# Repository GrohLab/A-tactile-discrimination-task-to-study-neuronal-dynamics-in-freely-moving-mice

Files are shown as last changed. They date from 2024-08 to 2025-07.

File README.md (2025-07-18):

#### Supplementary Materials for Heimburg, F., Saluti, N. M., Timm, J., Adlakha, A., Castelanelli, M., Klumpp M., Embray L., Both M., Draguhn A., Kuner T., Groh A. (2024). A tactile discrimination task to study neuronal dynamics in freely-moving mice.

**3D Model Files**: Contains 3D model blender files that show the proportions of the setup to scale.

**DataAndScripts**: Contains all required scripts and raw data (**.\RawData**) for replicating the figure legends.

**MaterialList**: Includes relevant setup items and experimental components necessary for reproducing the experiments.



The publication of the study can be found here: https://www.nature.com/articles/s41467-025-61792-0

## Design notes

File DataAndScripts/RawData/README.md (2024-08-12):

#### This folder contains the necessary raw data, used by the MATLAB scripts in the parent folder.

| File               | Description                                                                                      |
|--------------------|--------------------------------------------------------------------------------------------------|
|animalData.mat      |Conatins the read out of behavioral data, such as performance, trial number, or learning speed.   |
|AnimalData_CalciumImaging.mat      |Contains calcium imaging data for the sample session for the sample animal imaged with miniscope.   |
|decodingAccuracy_Ephys.mat      |Contains the decoding accuracies of lidocaine and control sessions. Rows resemble accuracies of different time windows, columns resemble the different recording areas (i.e., BC, VPM, POm, and ZIv).   |
|FrameInfo_OverviewVideo.mat      |Contains the animal's positional data from an exemplary video, in order to plot positional heat-maps and velocity plots.   |
|ROC_metrics_whiskerAngle.mat      |Contains the ROC metrics from the whisker angle decoding, from 100 bootstrapped runs.   |

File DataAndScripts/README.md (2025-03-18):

#### This folder contains all necessary Matlab files, used for obtaining the relevant figure data. Raw data is provided in a separate folder.

| File                                  | Description                                                                                                               |
|---------------------------------------|---------------------------------------------------------------------------------------------------------------------------|
| analyzePositionalData.m               | Loads the positional data from the RawData directory and generates a heat map of positional data and mean velocity plots. |
| Backlights.m                          | Compares population performance with and without backlights.                                                              |
| CNN_decoder_forCalciumImaging.m       | Code to train the CNN decoder and plot relevant figures in S3.                                                            |
| decreasing_contrast.m                 | Compares population performance across contrasts.                                                                         |
| Ephys_WhiskerMetrics.m                | Correlates ephys activity with behavioral metrics (e.g., whisker-angle, whisking-phase)                                   | 
| ExpNaive_TrialCount.m                 | Counts trials per animal for initial and reversed rule.                                                                   |
| Extinction.m                          | Compares population performance before and after extinction.                                                              |
| LearningInstability.m                 | Calculates the learning instability of mice with ablated BC.                                                              | 
| LearningSpeed.m                       | Compares learning speed and time between contrasts and between rules.                                                     |
| LearningSpeed_Cohort12.m              | Compares learning time for only cohort 12 (repeated rule switches)                                                        |
| Licking_Behavior.m                    | Analyzes and visualizes lick rates for mice across different stages of an experiment.                                     |
| Lidocaine.m                           | Compares population performance with and without lidocaine application.                                                   |
| NumSesperAnimal.m                     | Counts number of sessions per animal for initial and reversed rule.                                                       |
| onsetLatencyAnalysis.m                | Calculates the onset latency of ephys activity after aperture-touch.                                                      |
| Population_Analysis.m                 | Plots population performance over trials.                                                                                 |
| Population_Analysis_Cohort12.m        | Plots population performance over trials for only cohort 12 (repeated rule switches).                                     |
| Population_Analysis_Cohort16.m        | Plots population performance over trials for only cohort 16 (contrast 14 mm and 16 mm).                                   |
| Scripts_for_figures_calciumimaging.m  | Plot all the figures for Figure 3 calcium imaging data                                                                    |
| whiskerpluck.m                        | Compares population performance before and after whiskerpluck.                                                            |

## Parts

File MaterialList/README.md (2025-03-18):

### This table contains all materials, that were used throughout the course of the experiments. 

#### Linear Maze
| Product                                                                                      | Supplier                                        |
|----------------------------------------------------------------------------------------------|-------------------------------------------------|
| Linear track ([82 x 10 cm](Track%20complete%20with%20measurements.jpg), wood)                | Custom built, Lee Embray, Heidelberg            |
| Controlling unit of the behavioral apparatus (Arduino Uno R3 with firmata firmware)          | Arduino, assembled by Lee Embray, Heidelberg    |
| Metal wings (height: 205 mm, width: 97 mm, aluminum)                                         | Lee Embray, Heidelberg                          |
| [Controlling unit of the apertures with stepper motors](ApertureGate/info.md)                | Lee Embray, Heidelberg                          |

#### Lick ports adapted from Cornelius Schwarz, Tübingen
| Product                                                                                      | Supplier                                        |
|----------------------------------------------------------------------------------------------|-------------------------------------------------|
| Vasofix® Safety Braunüle® FEP G16                                                            | B. Braun SE, Melsungen, Germany                 |
| Piezo sensor (#285-784)                                                                      | RS components GmbH, Mörfelden-Walldorf, Germany |
| Analog-to-digital converter (ADC) to control lick ports                                      | Cornelius Schwarz, Tübingen                     |

#### Sensors and IR illumination 
| Product                                                                                      | Supplier                                        |
|----------------------------------------------------------------------------------------------|-------------------------------------------------|
| [Light beams](LightBeams/info.md)                                                            | Lee Embray, Heidelberg                          |
| LED strips for overhead illumination (Synergy 21 LED Flex Strip infrarot IR 12 12V IP65 Security Line 850nm, #140455) | ALLNET GmbH, Germering, Germany  |
| Backlight LEDs (HT-110IRPJ IR-Emitter 850 nm 140° 1204 SMD)                                  | Harvatek Corporation, Hsinchu, Taiwan           |
| Diffuser plate (3D printed with clear FLGPCL04 and sanded with P600)                         | Formlabs GmbH, Berlin, Germany                  |
| Diffuser film, 60% light diffusion (#DSF-10)                                                 | Folien Fischer UG, Hamburg, Germany             |

#### Intervention drugs
| Product                                                                                      | Supplier                                        |
|----------------------------------------------------------------------------------------------|-------------------------------------------------|
| Isoflurane (Isofluran Baxter)                                                                | Baxter Deutschland GmbH, Germany                |
| Buprenorphine (Bupresol vet. Multidose 0,3 mg/ml, 10 ml)                                     | CP-Pharma Handelsgesellschaft mbH, Burgdorf, Germany |
| Ketamine (100 mg/ml, 10 ml)                                                                  | CP-Pharma Handelsgesellschaft mbH, Burgdorf, Germany |
| Xylazine (Xylavet® 20 mg/ml)                                                                 | CP-Pharma Handelsgesellschaft mbH, Burgdorf, Germany |
| Lidocaine (Xylocaine® 1%)                                                                    | Aspen Pharma Trading Limited, Ireland           |
| ssAAV-1/2-hSyn1-chI-GCaMP6f-WPRE-SV40p(A)                                                    | Viral Vector Facility (VVF), Zürich, Switzerland|
| N-Methyl-D-aspartic acid, 98% (#AC329190500)                                                 | Thermo Fisher Scientific Inc., MA, USA          |

#### Cameras
| Product                                                                                      | Supplier                                        |
|----------------------------------------------------------------------------------------------|-------------------------------------------------|
| 2x High speed cameras (DMK 37BUX287)                                                         | The Imaging Source Europe GmbH, Bremen, Germany |
| Overview camera (DMK 37BUX290)                                                               | The Imaging Source Europe GmbH, Bremen, Germany |

#### Reward / punishment
| Product                                                                                      | Supplier                                        |
|----------------------------------------------------------------------------------------------|-------------------------------------------------|
| [Food dispensers](FoodDispensers/info.md)                                                    | Lee Embray, Heidelberg                          |
| 2 ml syringes (BD Discardit II)                                                              | Becton Dickinson GmbH, Heidelberg, Germany      |
| Tubes with Luer connector (#4256000)                                                         | B. Braun SE, Melsungen, Germany                 |
| Hifi integrated amplifier (A-S301)                                                           | Yamaha Music Europe GmbH, Rellingen, Germany    |
| 2x Speakers (Neo X 3.0 ribbon tweeter)                                                       | Fountek Electronics Co., Ltd, Zhejiang, China   |

#### EIB
| Product                                                                                      | Supplier                                        |
|----------------------------------------------------------------------------------------------|-------------------------------------------------|
| RHD USB Interface Board (#C3100)                                                             | Intan Technologies, CA, USA                     |
| Samtec Male Connector EIB (ST4-40-1.00-L-D-P-TR)                                             | Samtec Europe GmbH, Germering, Germany          |
| Samtec Female Connector Headstage (SS4-40-3.00-L-D-K-TR)                                     | Samtec Europe GmbH, Germering, Germany          |
| PCB (EIB and headstage)                                                                      | Custom built ([BRD file](EIB64-ST4-Multi.brd), printed by Multi-Circuit-Boards Ltd, Munich, Germany |
| Tungsten 99.95% CS Wire for Tetrodes (#100211)                                               | California Fine Wire Company, CA, USA           |
| Gold chloride solution for gold plating (200 mg/dL gold chloride in deionized water, HT1004-100ML) | Sigma-Aldrich, Inc., MO, USA              |
| Intan Interface 64 Channel Amplifier Chip (RHD2164)                                          | Intan Technologies, CA, USA                     |
| UV-curable adhesive (3M™ Filtek™ Supreme XTE)                                                | 3M Deutschland GmbH, Neuss, Germany             |
| Function generator (A365 Stimulus Isolator)                                                  | World Precision Instruments, Inc., FL, USA      |
| Electric Rotary Joint (AHRJ-OE_2x2_AD_200-0.22_24_USB-C)                                     | Doric Lenses Inc., Quebec City, Canada          |

#### Miniscope
| Product                                                                                      | Supplier                                        |
|----------------------------------------------------------------------------------------------|-------------------------------------------------|
| Miniscope V4 main body (Excitation, objective, and emission module)                          | Custom print from Heidelberg precision mechanics workshop/ Open Ephys |
| V4 Base Plate                                                                                | Custom print from Heidelberg precision mechanics workshop/ Open-Ephys |
| Rigid-Flex PCB                                                                               | Open-Ephys                                      |
| Optical Filters <br> - Excitation filter 4mm x 4mm, ET474/40x <br> - Emission filter 4mm x 4mm, ET525/50m <br> - Dichroic mirror 6mm x 4mm, T495lpxr | Chromal/Open-Ephys |
| Lenses <br> - 2 x 3mm diameter, 6mm FL achromat used in the objective module (#45-089) <br> - 4mm diameter, 10mm FL achromat used in the emission module (#63-691) <br> - Half-ball Lens, 3.0mm Diameter, N-BK7 (#47-269)                                    | Edmund Optics/Open-Ephys                        |
| Coax cable, 36AWG 26/50SPC                                                                   | Cooner Wire                                     |
| Hirose U.FL Connector, U.FL-PR-SMT2.5-1(10)                                                  | Mouser                                          |
| GRIN Lenses, ProView™ Lens Probe, 0.5mm diameter, ~4.0mm length                              | Inscopix                                        |

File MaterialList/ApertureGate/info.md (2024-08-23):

# Adjustable Aperture Gate

## Description

The Adjustable Aperture Gate is designed to produce multiple programmable apertures between two sliding doors for use in rodent behaviour experiments.
The various apertures can be pre programmed using the programming module, the programming module can then be used to test the operations using the DIP switches on it's front panel,
once the programming module is disconnected and the unit connected to experiment controller (external controller) these preset distances between the sliding doors can then be
 recalled using three 5V TTL (Transistor-Transistor-Logic) or 3.3V logic inputs driven by a single board computer (Raspberry Pie or Arduino for example) or any other microprocessor or logic controller.

The unit requires a 12V power supply and three logic control inputs with ground, a simple three bit binary word input will recall the various presets causing the sliding doors to move to the selected distance.

The design has two parts, the **Programming Module** (LCD/Buttons) and the **Gate Unit** (Mechanical/Main PCB) which are connected together using a standard one-to-one 15pin D type male to female cable.
The LCD and switches are mounted in a small housing allowing parameter changes without disturbing the experiment.
The Gate Assembly unit is designed using Google Sketchup and 3D printed using a FormLabs Form 2 SLA (Stereolithografie) 3D printer,
assembly of the mechanical parts is quite labour intensive and modification of the motor for this application requires the use of a lathe.

The Programming Module only needs to be connected to change the preset aperture or to run tests to check operation, all changes are then saved to non volatile memory in the Gate Unit and the Gate
Unit can then run without the programming module.
Therefore only one Programming Module is necessary to operate multiple Gate Units.

## Programming Module

## Parts List 1

|Part | Qty |Part Description  | Manufacturer | Part ID | Order URL |
| ---- | --- | ----------------- | ------------ | ------- | --------- |
| J1 | 1 | DSUB 15M connector | MH Connectors | 746751 | [Conrad](https://www.conrad.de/de/p/mh-connectors-mhdb15-sp-2101-0180-02-d-sub-stiftleiste-180-polzahl-num-15-loetkelch-1-st-746751.html) |okw-soft-case-d9052288-wall-mount-enclosure-desktop-case-73-x-117-x-27-acrylonitrile-butadiene-styrene-lava-volcano-1-531612) |
| LCD1 | 1 | LCD 16x2 White on Blue  | Gleichmann | 183045 | [Conrad](https://www.conrad.com/p/gleichmann-led-component-white-blue-w-x-h-x-d-80-x-36-x-132-mm-ge-c1602b-tmi-jtr-183045) |
| SW1-4 | 4 | Momentary Switch TC-D6SW  | TRU COMPONENTS | 2238782 | [Conrad](https://www.conrad.de/de/p/tru-components-tc-d6sw-impulstaster-35-v-dc-0-01-a-tastend-1-st-1589415.html) |
| DSW1 | 1 | DIP Switch 4 Way  | APEM | 700640 | [Conrad](https://www.conrad.com/p/apem-nds-04-v-dip-switch-standard-700640) |
| R1 | 1 | Resistor 56 Ohm 1/4W | Yageo | 1417715 | [Conrad](https://www.conrad.com/p/yageo-cfr-25jt-52-56r-carbon-film-resistor-56-axial-lead-0207-025-w-5-1-pcs-1417715) |
| R2,3,4 | 3 | Resistor 2.2k Ohm 1/4W | Yageo | 1417683 | [Conrad](https://www.conrad.com/p/yageo-cfr-25jt-52-2k2-carbon-film-resistor-22-k-axial-lead-0207-025-w-5-1-pcs-1417683) |
| RV1 | 1 | Trim Potentiometer 10k Ohm 1/4W  | Vishay | 423980 | [Conrad](https://www.conrad.com/p/vishay-t63yb103kt20-t63yb103kt20-multi-grade-trim-potentiometer-423980) |
| PCB | 1 | Strip Board Paper/Copper 2.54mm | Rademacher | 529531-62 | [Conrad](https://www.conrad.de/de/p/rademacher-wr-typ-710-2-platine-hartpapier-l-x-b-100-mm-x-75-mm-35-m-rastermass-2-54-mm-inhalt-1-st-529531.html) |
| Case | 1 | Case 73x117x27mm  | OKW | 531612 | [Conrad](https://www.conrad.com/p/okw-soft-case-d9052288-wall-mount-enclosure-desktop-case-73-x-117-x-27-acrylonitrile-butadiene-styrene-lava-volcano-1-531612) |

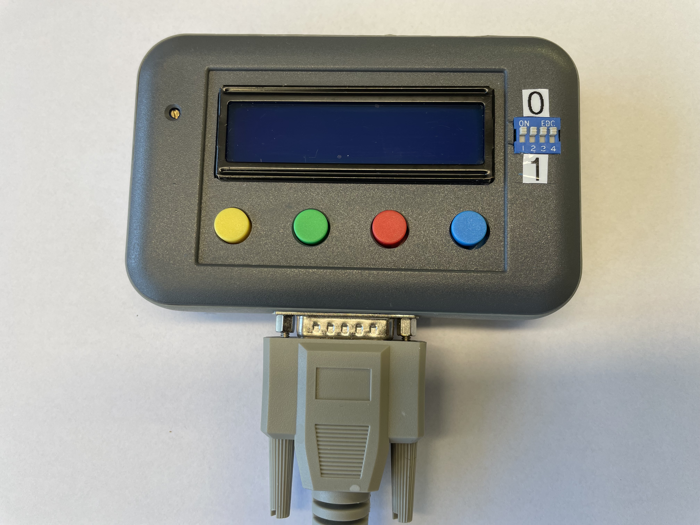
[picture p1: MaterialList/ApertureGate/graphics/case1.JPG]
programmer Case
<br/>**Programming Module**

The programming module is created using the following schematic, a small piece of strip board is used to mount the four main switches as shown in the picture below.
All components are mounted directly onto the LCD or switches therefore no PCB is necessary for the programming module.
The potentiometer RV1 is used to adjust the contrast on the LCD and is required to be set only once.
D1 is the backlight that is built into the LCD module and connected using pins 15 and 16 of the LCD module.

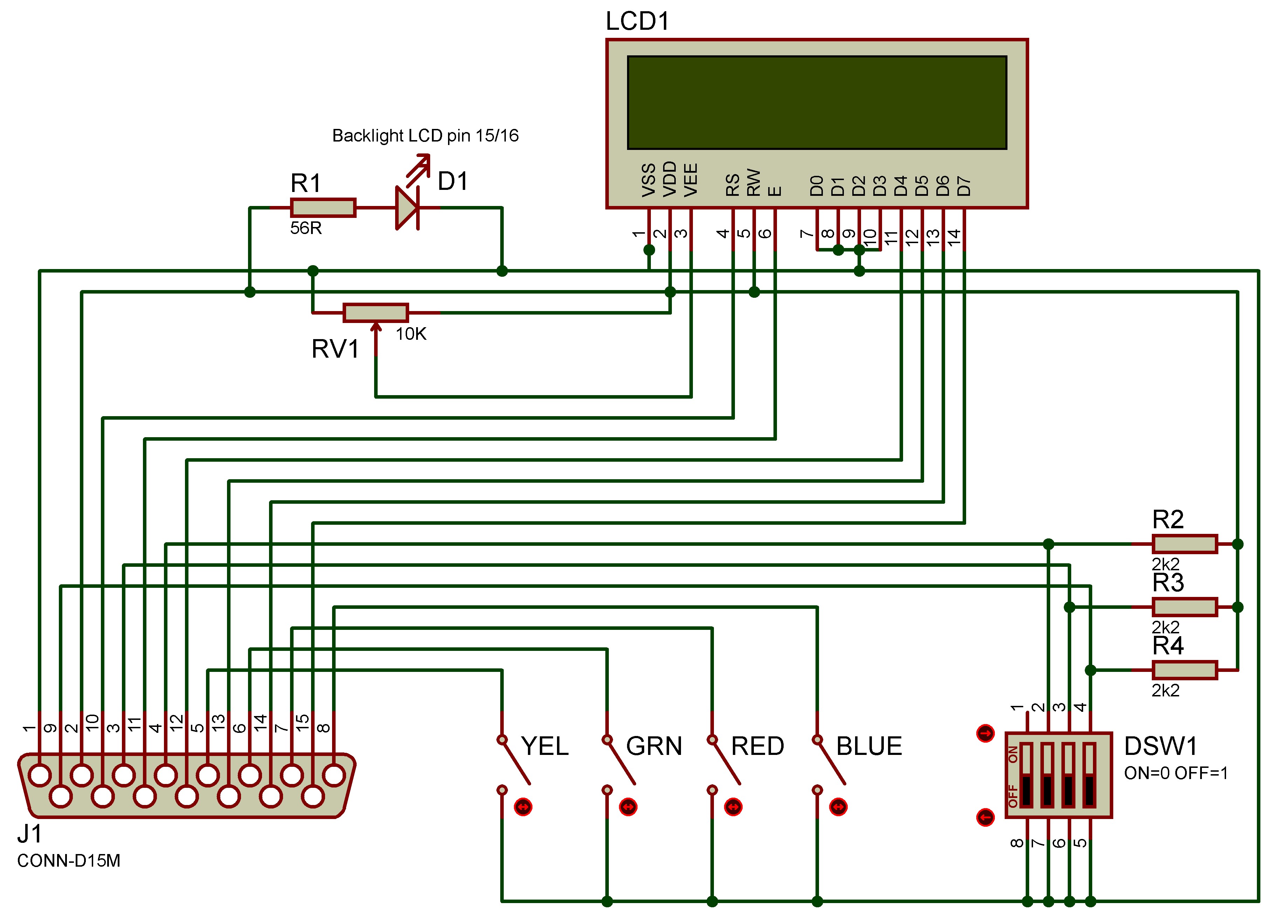
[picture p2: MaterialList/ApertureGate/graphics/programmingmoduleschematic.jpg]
Programming Module Schematic
<br/>**Programming Module Schematic**

All components are mounted in a plastic housing and necessary holes for the the LCD, switches and connectors are drilled accordingly.

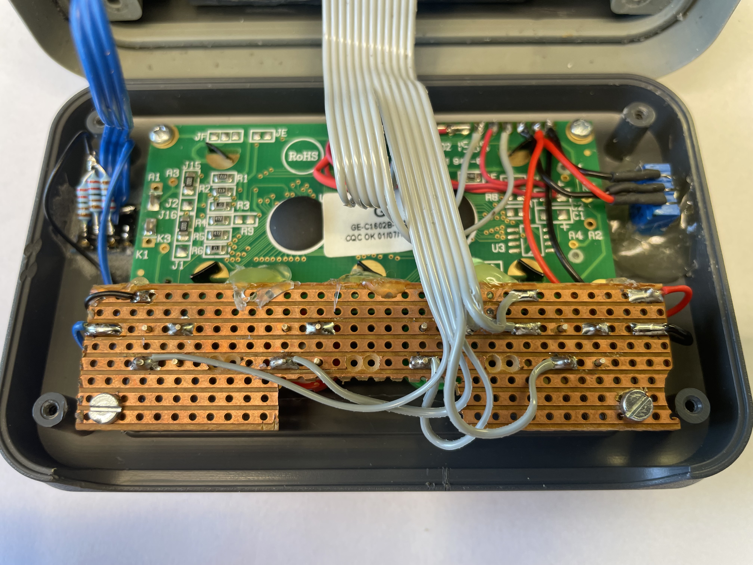
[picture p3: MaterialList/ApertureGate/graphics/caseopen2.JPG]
case open2
<br/>**Programming Module - Open**

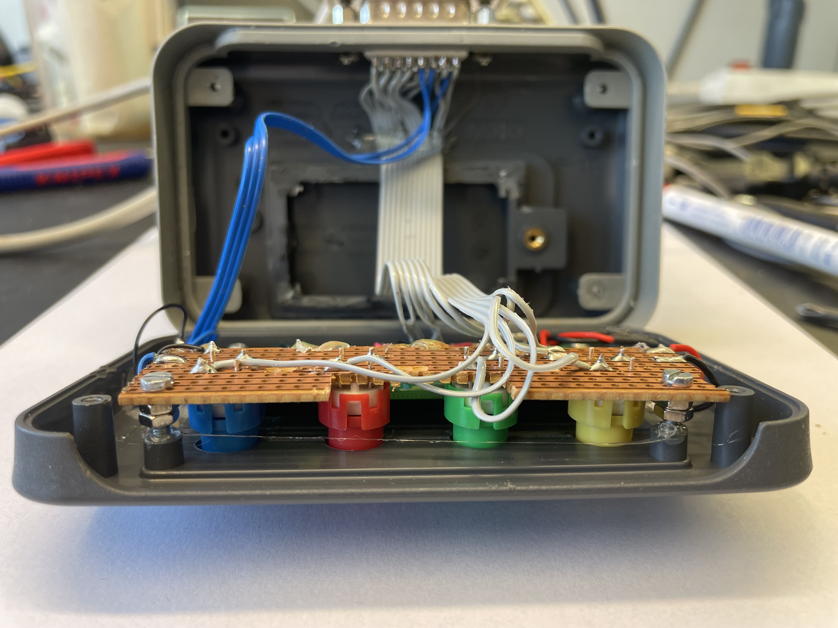
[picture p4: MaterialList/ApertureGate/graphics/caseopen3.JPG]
case open3
<br/>**Programming Module - Button Mounting**

## Gate Unit

## Parts List 2

|Part | Qty |Part Description  | Manufacturer | Part ID | Order URL |
| ---- | --- | ----------------- | ------------ | ------- | --------- |
| U1 | 1 | Microchip PIC18F23K20 MPU | Microchip  | 666-9860 | [RS Components](https://de.rs-online.com/web/p/mikrocontroller/6669860) |
| U2 | 1 | L297D Stepper Motor Driver SOIC | STMicroelectronics  | 102-3535  | [RS Components](https://de.rs-online.com/web/p/motor-treiber-ics/1023535) |
| U3 | 1 | L298P013TR Dual Full Bridge Driver | STMicroelectronics | 880-5308 | [RS Components](https://de.rs-online.com/web/p/motor-treiber-ics/8805308) |
| U4 | 1 | SMD 3.3V Regulator TLV111733 | Texas Instruments | 923-3827 | [RS Components](https://de.rs-online.com/web/p/spannungsregler/9233827) |
| U5 | 1 | L78S05CV 5V Regulator TO220 | STMicroelectronics  | 179345  | [Conrad](https://www.conrad.de/de/p/stmicroelectronics-l78s05cv-spannungsregler-linear-typ78-to-220ab-positiv-fest-5-v-2-a-179345.html) |
| D1-8 | 8 | Schottkey Diode SK26L | PanJit | 1304995 | [Conrad](https://www.conrad.de/de/p/panjit-schottky-diode-gleichrichter-sk26l-do-214aa-60-v-einzeln-1304995.html) |
| R1,2 | 2 | Resistor SMD 1206 1 Ohm 1/2W | Panasonic | 1473248 | [Conrad](https://www.conrad.de/de/p/panasonic-erj-8bqf1r0v-dickschicht-widerstand-1-smd-1206-0-5-w-1-200-ppm-c-1473248.html) |
| R3 | 1 | Resistor SMD 0805 22k Ohm 1/8W| Tru Components | 1584677 | [Conrad](https://www.conrad.de/de/p/dickschicht-widerstand-22-k-smd-0805-0-125-w-5-100-ppm-c-tru-components-tc-0805s8j0223t5e203-1-st-1584677.html) |
| R5 | 1 | Resistor SMD 0805 3.3k Ohm 1/8W| Tru Components | 1584493 | [Conrad](https://www.conrad.de/de/p/tru-components-tc-0805s8f3301t5e203-dickschicht-widerstand-3-3-k-smd-0805-0-125-w-1-100-ppm-c-1-st-tape-cut-1584493.html) |
| R4,6-13 | 9 | Resistor SMD 0805 2.2k Ohm 1/8W| Tru Components | 1584491 | [Conrad](https://www.conrad.de/de/p/tru-components-tc-0805s8f2201t5e203-dickschicht-widerstand-2-2-k-smd-0805-0-125-w-1-100-ppm-c-1-st-tape-cut-1584491.html) |
| C1 | 1 | Capacitor SMD 0805 3300pF | Thomsen | 460338 | [Conrad](https://www.conrad.de/de/p/thomsen-keramik-kondensator-smd-0805-3300-pf-50-v-10-1-st-tape-cut-460338.html) |
| C2,3,5,7 | 4 | Capacitor SMD 0805 100nF 50V  | Samsung | 454108 | [Conrad](https://www.conrad.de/de/p/samsung-electro-mechanics-cl21b104jbcnnnc-keramik-kondensator-smd-0805-100-nf-50-v-5-4000-st-tape-on-full-reel-454108.html?searchType=SearchRedirect) |
| C4 | 1 | Elecrolytic Capacitor 470uF 16V| Yageo | 445373 | [Conrad](https://www.conrad.de/de/p/yageo-se016m0470b3f-0811-elektrolyt-kondensator-radial-bedrahtet-3-5-mm-470-f-16-v-20-x-h-8-mm-x-12-mm-1-st-445373.html) |
| C6 | 1 | Elecrolytic Capacitor 100uF 16V| Yageo | 445579 | [Conrad](https://www.conrad.de/de/p/yageo-s5016m0100bzf-0605-elektrolyt-kondensator-radial-bedrahtet-2-5-mm-100-f-16-v-20-x-h-6-mm-x-5-mm-1-st-445579.html) |
| J1-6 | 4 | Pin Strip Header 8Pin Male| BKL Electronic | 742235-VQ | [Conrad](https://www.conrad.com/p/bkl-electronic-10120504-straight-nominal-current-details-3-a-742235) |
| J1-6 | 4 | Pin recepticle 8Pin Female | TRU COMPONENTS | 1560801 | [Conrad](https://www.conrad.com/p/tru-components-receptacles-precision-no-of-rows-1-pins-per-row-8-tc-0306pf-008-1-50-00-1-pcs-1560801) |
| J7 | 1 | D15F connector | MH Connectors | 746800 | [Conrad](https://www.conrad.de/de/p/mh-connectors-mhdb15-ss-2101-0180-12-d-sub-buchsenleiste-180-polzahl-num-15-loetkelch-1-st-746800.html) |
| J8 | 1 | Low Power connector Socket 2.1mm 5.5mm | BKL Electronic | 733946 | [Conrad](https://www.conrad.com/p/bkl-electronic-072335-low-power-connector-socket-vertical-vertical-55-mm-21-mm-1-pcs-733946) |
| PSU | 1 | Powersupply 12V 3A  | Mean Well | 1439200 | [Conrad](https://www.conrad.de/de/p/mean-well-gst36e12-p1j-steckernetzteil-festspannung-12-v-dc-3000-ma-36-w-1439200.html) |
| M1 | 1 | Stepper Motor 0.25Nm 0.6A | EMIS | 198398 | [Conrad](https://www.conrad.de/de/p/emis-schrittmotor-103-h5205-0351-103-h5205-0351-0-25-nm-0-6-a-wellen-durchmesser-5-mm-198398.html) |
| SW5,6 | 2 | Microswitch125V AC 3A| Hartmann | 704713 | [Conrad](https://www.conrad.de/de/p/hartmann-mikroschalter-microhart-125-v-ac-3-a-1-x-ein-ein-tastend-1-st-704713.html) |
| Tube 5mm | 1 | Brass Tube 5mmx500mm  | REELY | 221794 | [Conrad](https://www.conrad.com/p/brass-tube-rail-x-l-5-mm-x-500-mm-inside-diameter-3-mm-1-pcs-221794) |
| Rod 6mm | 1 | Silver Steel Rod 6mmx500mm  | REELY | 237086 | [Conrad](https://www.conrad.com/p/reely-silver-steel-shaft-x-l-6-mm-x-500-mm-237086) |
| Collared Bush | 2 | ID-6mm OD-10/15mm  | REELY| 237043 | [Conrad](https://www.conrad.com/p/reely-collared-bush-inside-diameter-6-mm-outside-diameter-10-mm-width-15-mm-1-pcs-237043) |
| Spindle | 1 | RH Threaded Spindle TSR-Tr 5x1.5  | HFB| 12-0515-01 | [HFB](https://hfbshop.de/?cat=c27_TSR-1500mm-Rechts-TSR-1500mm-Rechtsgewinde.html) |
| Spindle | 1 | LH Threaded Spindle TSR-Tr 5x1.5  | HFB| 12-0515-02 | [HFB](https://hfbshop.de/?cat=c30_TSR-1500mm-Links-TSR-1500mm-Linksgewinde.html) |
| Spindle Nut | 1 | RH Nut 5x1.5 | HFB| 33-0515-01 | [HFB](https://hfbshop.de/product_info.php?info=p5076_sechskant-messingmutter-rohling-skm-ms-tr-5x1-5-rechts.html) |
| Spindle Nut | 1 | LH Nut 5x1.5  | HFB| 33-0515-02 | [HFB](https://hfbshop.de/product_info.php?info=p5098_sechskant-messingmutter-rohling-skm-ms-tr-5x1-5-links.html) |
| Bearing | 2 | Radial 3x10x4  | REELY | 215210 | [Conrad](https://www.conrad.com/p/reely-radial-ball-bearing-chrome-steel-inside-diameter-3-mm-outside-diameter-10-mm-rotational-speed-max-60000-um-215210) |
| Cable | 1 | D-Sub15 Cable M-F 1M  | Pheonix Contact | 673800 | [Conrad](https://www.conrad.de/de/p/phoenix-contact-seriell-parallel-anschlusskabel-1x-d-sub-buchse-15pol-1x-d-sub-stecker-15pol-1-00-m-weiss-673800.html) |
| Wire | 1 | Jumper Wire 1x0.2mm  | Tru Components | 1567899 | [Conrad](https://www.conrad.de/de/p/tru-components-1567899-schaltdraht-yv-1-x-0-20-mm-schwarz-100-m-1567899.html) |

## 1. PCB Assembly

PCB Gerber files are supplied allowing production and ordering, the origional Proteus design file is also supplied incase any modifications for specific requirements are necessary.
All components of the PCB are mounted by hand and special attention should be applied to the motor driver (U3) as the underside of the component is used as a heat sink and must be soldered to the PCB,
this is done from the reverse side of the PCB using the through holes integrated on the PCB design. Soldering SMD devices by hand requires some experience.

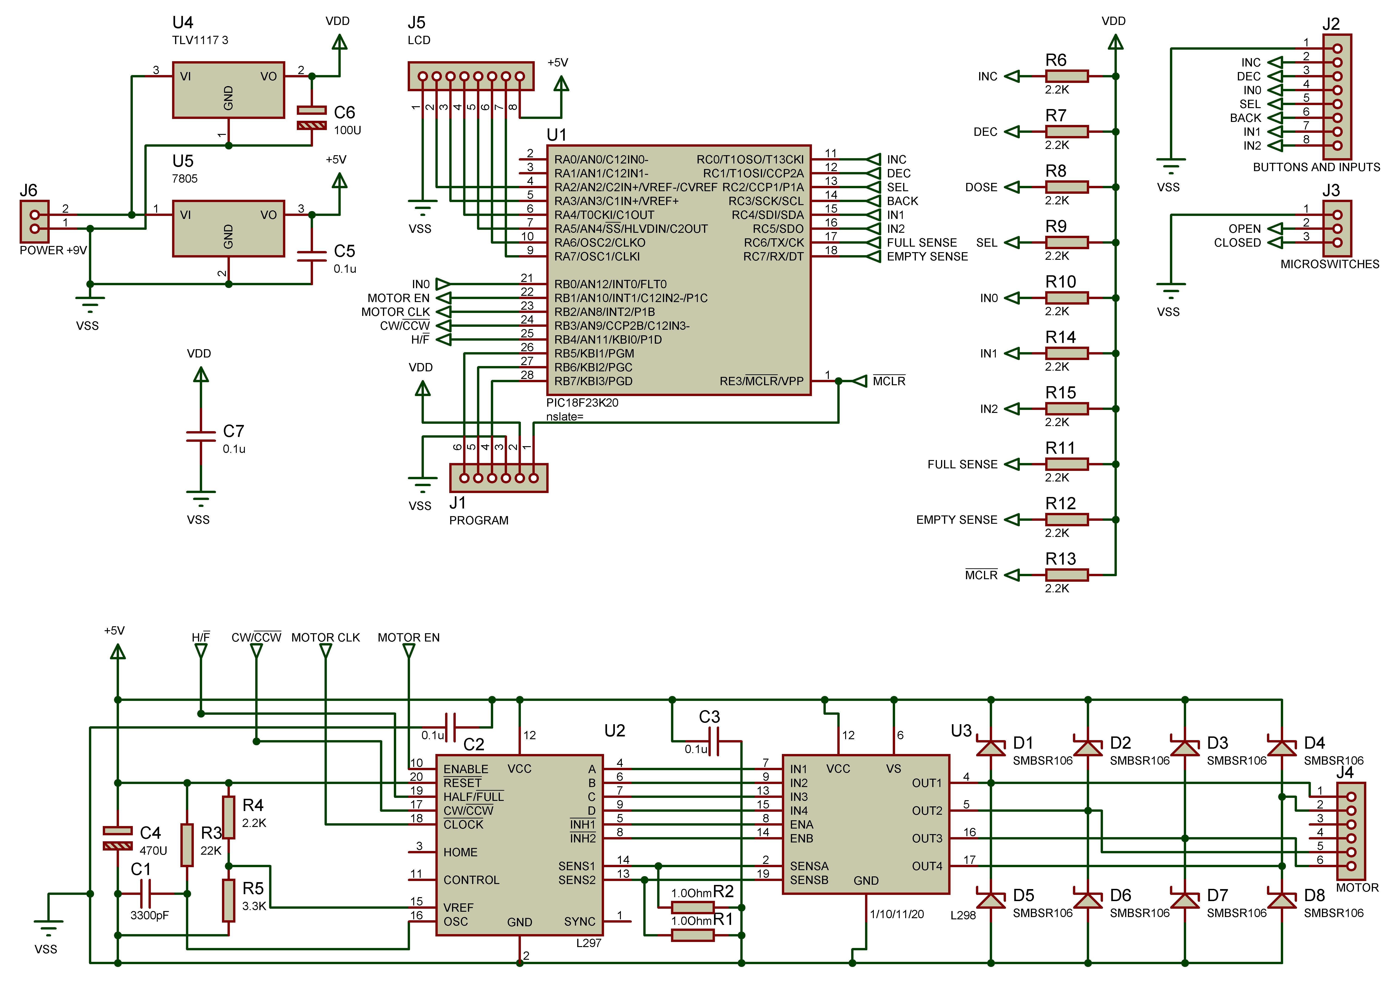
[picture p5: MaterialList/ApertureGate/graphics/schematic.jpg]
schematic
<br/>
**Main PCB Schematic**

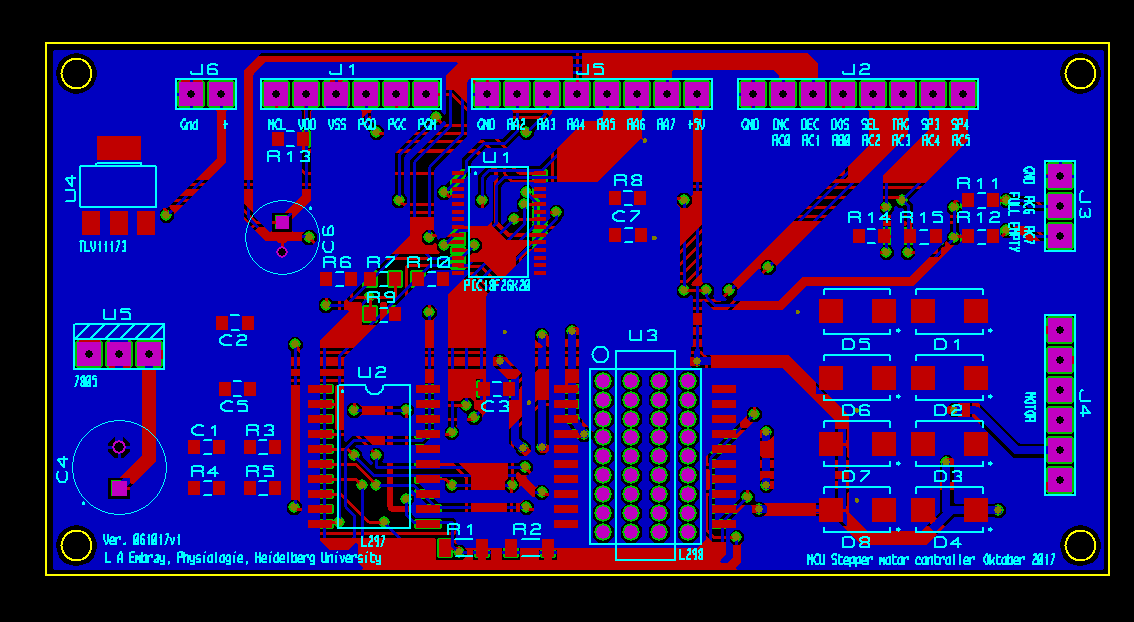
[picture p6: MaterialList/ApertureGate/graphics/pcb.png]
pcb
<br/>
**Main PCB Layout**

## 2. Programming

The Microprocessor must be programmed with the included program, this is performed using a Microchip Pickit 3 In-Circuit Debugger/Programmer and the Microchip MPLAB IDE X software.
once the included project is added to the programming software the PicKit programmer can be plugged directly into the J1 on the main PCB and the program uploaded to the microprocessor.

## 3. Parts Preparation

The output shaft of the motor **(22)** requires modification, this is best performed on a lathe, The motor should be carefully dismantled and the rotor removed.

1. Using a lathe the shaft of the rotor should be shortened to the same length as the shorter side of the rotor meaning the assembled motor has no protruding shaft from either side.
2. Using a lathe the complete length of the rotor/shaft should be drilled out using a 2.5mm drill bit mounted in the tailstock,
3. it is very important that the drilling is centered correctly for smooth operation and this can be achieved by using a centre drill first as a guide before the 2.5mm drill bit.
4. Using a lathe an M3 thread must be cut within the hole drilled in step two, the M3 Tap should be mounted in the tailstock and the tailstock should be freely moving on the guide ways,
5. by manually turning the main spindle chuck holding the rotor the thread can be accurately cut through the entire length of the rotor shaft.
6. The motor should now be reassembled paying particular care to making sure there is no small pieces of metal swarf trapped within and all parts are sufficiently clean,
7. any dirt or swarf will cause the motor to jam.

The two Silver Steel Shafts **(17)** should be cut to a length of 202mm, using a lathe the ends of the shafts should be drilled to a depth of 10mm using a 3.3mm drill,
these holes should then be tapped using a M4 tap.

A piece of 5mm brass tube **(6)** should be cut to a length of 72.5mm, this is used to carry and protect the two wires that connect to the end of travel switch **(4)** as shown in the picture below.

The left and right threaded rods (8,18) should be cut to a length of 88mm.

1. Using a lathe 4mm of the ends of the rods should be reduced in diameter to 3mm.
2. Using a lathe, 10mm of the opposite end of the rods should be reduced to a diameter of 3mm.
3. Using a lathe and an M3 die the 10mm end should have a M3 thread cut.

Once all parts are 3D printed a small amount of cleaning/trimming and sanding is required to allow all parts to accurately fit together without force. The following drawing shows all parts for assembly.

The four motor mount holes on the Main Body **(12)** should be counter sunk to allow for flush mounting of the motor allowing the slider **(10)** to travel up against the Main Body **(12)** without obstruction.

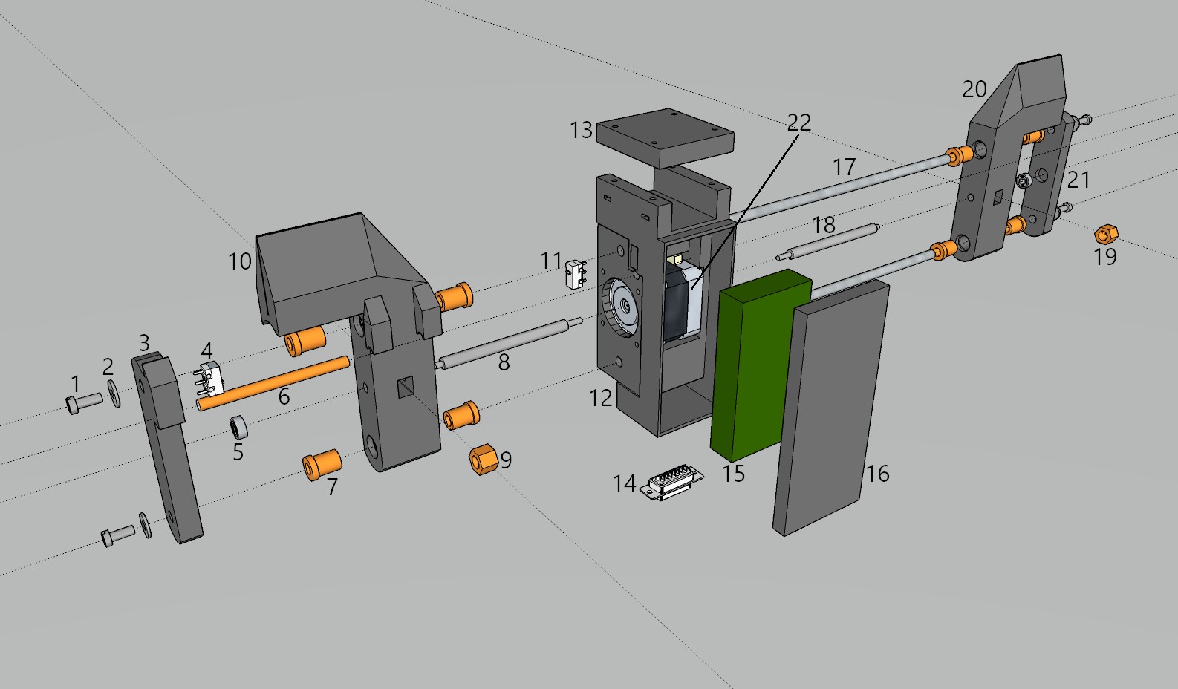
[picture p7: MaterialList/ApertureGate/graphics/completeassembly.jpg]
<br/>
**Complete Assembly**

## Key To Drawing

1. M4x10mm Screw x4
2. M4 Washer x4
3. Left Slider Stop
4. End of Travel Micro Switch
5. Bearing Radial 3x10x4 x2
6. Brass Tube 5x72.5mm
7. Collared Bush 6x10x15mm x8
8. Left Hand Threaded Rod
9. Left Handed Brass Nut 5x1.5
10. Left Slider
11. Start of Travel Micro Switch
12. Main Body
13. Mounting Clamp
14. D15 Female Connector
15. Assembled Printed Circuit Board
16. PCB Cover
17. Silver Steel Shaft 6x202mm x2
18. Right Hand Threaded Rod
19. Right Handed Brass Nut 5x1.5
20. Right Slider
21. Right Slider Stop
22. Motor

## 4. Assembly of parts

1. The Motor **(22)** is inserted into the Main Body **(12)** and fixed in place with the wires facing upwards using four M3x10 counter sunk screws.

2. The two Silver Steel Shafts **(17)** are inserted into the Main Body **(12)** with equal lengths of the shaft protruding from each side of the Main Body **(12)**,
these should now be fixed in place using cyanoacrylate glue being careful not to get any excess glue on the Shafts **(17)**.

3. The two End Stop Microswitches **(4/11)** should be prepared by soldering two 0.05mm wires of 15cm length to each of of the Microswitches normally open contacts(no).

4. One Microswitch **(11)** can now be mounted into its cutout on the Main Body **(12)** and the wires threaded through to the PCB cavity inside the Main Body **(12)**,
the second Microswitch can now be inserted into the cutout on the Left Slider Stop **(3)** and the wires threaded through the channel inside the Left Slider Stop **(3)**,
for the time being the wires should be left long and will later be attached.

5. The eight Collared Bushes **(7)** should be carefully pressed into the Left and Right Sliders **(10/20)**, it is important that these are inserted straight and true,
this is best done using either a press or a machine vice using a scrap piece of the 6mm silver steel shaft as a guide,
opposing bushes should be pressed into place at the same time with the 6mm shaft inserted into both bushes as this will guarantee alignment during insertion.

6. The Left Handed and Right Handed Threaded rods **(8/18)** can now be attached to the Motor **(22)**,
the 10mm of M3 thread on the threaded rod should be screwed into the motors shaft using thread lock to be sure they don't unscrew.

7. The two Bearings **(5)** are to be pressed into the Left and Right Slider stops **(3/21)** this is easily accomplished using a machine or bench vice.

8. The Left and Right Hand Threaded Brass Nuts **(9/19)** can be installed into the Left and Right Sliders **(10/20)**,
the nuts should not be a tight fit but also should not have any excessive play as this will affect the accuracy of the aperture,
however a small amount of movement must be available to allow for slight inaccuracies in the Threaded Rods **(8/18)**.

9. The two Sliders **(10/20)** can now be slid onto the two Silver Steel Shafts **(17)** and with the Left and Right Handed Brass nuts **(9/19)** held in place can be slid until the
Brass Nuts come into contact with the Left and Right Handed Threaded Rods **(8/18)**.

10. By applying a small amount of pressure to both Sliders **(10/20)** and turning the Motor Shaft both the sliders will be drawn in towards the motor,
it is important that both Sliders arrive at the Main Body **(12)** at the same time, the Microswitch **(11)** should be heard to click just before the Sliders come into hard contact with the Main Body.

11. The Right Slider Stop **(21)** can now be fitted to the end of the Silver Steel Shaft **(17)** paying attention that the end of the Right Hand Threaded rod **(18)** is inserted into the
Bearing **(5)**, This can now be fixed in place using two M4x10 screws and washers **(1/2)** holding the Slider Stop to the two Shafts.

12. The Left Slider Stop **(3)** is mounted in exactley the same way with one exception,
the wires from the End Stop Microswitch **(4)** which were earlier threaded though the Left Slider Stop should now be threaded through the Brass Tube **(6)** and as the slider stop is brought into
place this tube should be inserted into the available holes on the Left Slider Stop **(3)** and the Main Body **(12)**, approximately 2.5mm of each end of the Brass Tube should be inserted.
The microswitch wire should be threaded through to the Main Body PCB cavity. The Slider Stop should be fixed into place using two M4x10 screws and washers **(1/2)**.

13. By turning the Motor/Threaded Rods the assembly can be checked for smooth operation and that the microswitches are pressed before the sliders make hard contact at either end of their travel,
a small amount of machine oil or grease should be applied to the threaded rods and also to the silver steel shafts.

14. The PCB **(15)** can now be placed within the cavity in the Main Body **(12)** with the wires from the two Microswitches **(4/11)** and Motor **(22)** exiting above the PCB.
The PCB **(15)** is a tight fit inside the Main Body **(12)** and does not require and additional fixing.

15. The wires from the Motor **(22)** should be cut and spliced (shortened) to a length that easily reaches the motor connector **(J4)** at the top of the PCB **(15)** without too much excess length,
this is now plugged into the motor connector **(J4)**.

16. The wires from the End Stop Microswitches **(4/11)** should be shortened and soldered to three pins of the female recepticle as shown in the diagram below,
this is then plugged into the end stop connector on the PCB **(J3)**.

17. The D15F **(J7)** is be prepared by soldering 10cm of wire on to each of the 15 pins,
this can then be mounted into the Main Body **(12)** with the wires exiting from the bottom of the PCB **(15)**,
the wires should then be connected to strips of female receptacle as shown in the diagram below, this can then be plugged into **(J5/J2)** on the PCB.

18. The Low power connector **(J8)** is prepared by soldering two wires (red and black) to the connector, The red wire is connected to the centre pin of the connector and the black to the ring,
the wires should exit inside the Main Body at the bottom of the PCB and shortened so that they easily reach the power connector on the PCB and then soldered to two pins of a female receptacle,
this can then be plugged into the power connector **(J6)** on the PCB.
The PCB **(15)** is a tight fit inside the Main Body **(12)** and does not require and additional fixing.

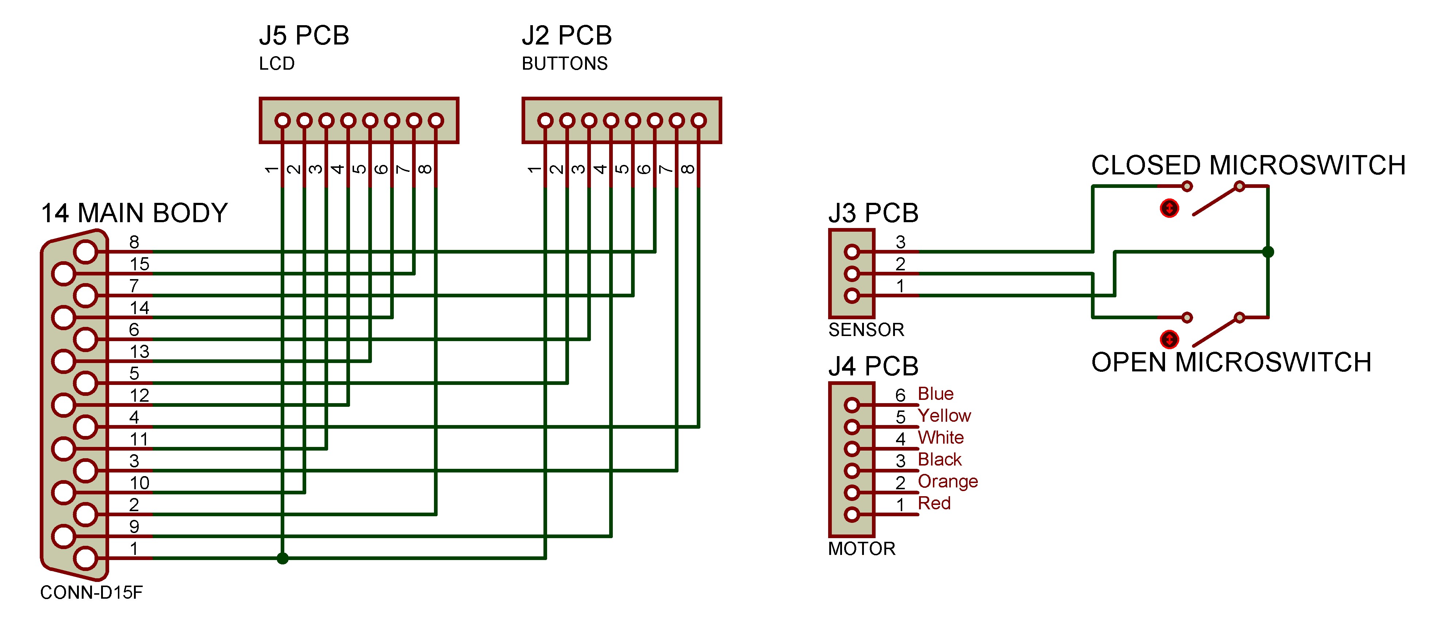
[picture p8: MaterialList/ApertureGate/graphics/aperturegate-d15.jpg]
<br/>
**Connections to PCB**

schematic<br/>
**Connections to PCB**

The gates themselves should be made to fit individual requirements, the gate holders on the sliders have been designed to accept 1mm aluminium sheet and fixed in placed using M3x25 screws and nuts.

## 5. Menus

 Once the power supply and programming module are connected the LCD will illuminate and the program will initiate. A simple menu structure for the operation is shown below.

running<br/>
**The first menu shows that the unit is running and waiting for an input change.**
Pressing SETUP will enter the function to adjust the presets of the different positions starting with position 0.**

running<br/>
**Pressing NEXT will change the selection to position 1 and then 2 up to position 7.**

running<br/>
**Pressing SEL on the selected position to be changed will enter the function to set the value for that preset.**

running<br/>
**Pressing + or - on the selected position will change the numerical value in millimeters for that position, pressing SEL to confirm will save this value to memory.**

## 6. Operation

Once the required presets have been entered using the Programming Module the positions can be checked using the DIP switches on the programming module.
The Gate Unit can be de-powered and the Programming Module removed, all parameters will be saved to Non-Volatile Memory.

Position 3 has been preset in the program to **Fake Move** and this mode will cause the doors to move away from the current position and then return to this position,
this has been done incase the sound of the motor creates a false stimulus/cue for the animal performing the experiment.
Position 7 is reserved and will always cause the doors to return **Home** thus closing the doors completely.
The two reseved positions can be modified in the program to allow eight user definable positions.

Using the diagram below a control cable can be built to allow the Gate Unit to be connected to a controller of choice as long as the controller presents a 3.3v or 5v 3bit logic output

The three bit binary logic inputs are as follows:

|Logic Input | Position Number  | Position |
| ---- | ----------------- | ----------- |
| 000 | Position 0 | User Definable 0-55mm |
| 001 | Position 1 | User Definable 0-55mm |
| 010 | Position 2 | User Definable 0-55mm |
| 011 | Position 3 | Fake Move |
| 100 | Position 4 | User Definable 0-55mm |
| 101 | Position 5 | User Definable 0-55mm |
| 110 | Position 6 | User Definable 0-55mm |
| 111 | Position 7 | Home/Closed |

schematic<br/>
**Control Pin Out for External Controller**

Once the power is re-applied the gates will follow the given logic inputs.

## Mounts

The Main Body **(12)** has been design for mounting on a 30x15mm rectangular steel tube present in our personal setup, the clamp **(13)** is screwed down tightly to achieve a tight fit,
the drawing can be modified before printing to allow for any other types of mounting requirements, orientation or position.

schematic<br/>
**Installed aperture gate**

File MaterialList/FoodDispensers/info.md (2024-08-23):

# Liquid Feeder

## Description

The liquid feeder is designed to administer a user defined preset amount of liquid food to rodents as a reward in behaviour experiments.
The liquid feeder can simply be integrated with any controller that offers a 5V TTL (Transistor-Transistor-Logic) or 3.3V logic output such as a single board computer (Raspberry Pie or Arduino for example)
 or any other microprocessor or logic controller. The feeder has an accuracy far higher than is actually necessary for the application at hand
 but allows the unit to have the possibility of many other applications such as automated administering of chemicals or drugs in a laborotary enviroment.

The unit requires a 9V power supply and a single logic control input with ground, a logic 1 pulse (High) will cause the liquid feeder to administer the user preset amount of liquid food
(Condensed Milk in our case) from the replaceable BD Discardit II 2ml syringe.

The design has two parts, the controller (Main PCB/LCD/Buttons) and the feeder (Mechanical) which are connected together using a standard one-to-one 9pin D type male to female cable.
The main PCB (printed circuit board), LCD and switches are mounted in a small housing allowing remote parameter changes without disturbing the experiment.
The Feeder unit is designed using Google Sketchup and 3D printed using a FormLabs Form 2 SLA (Stereolithografie) 3D printer,
assembly of the mechanical parts is quite labour intensive and modification of the motor for this application requires the use of a lathe.

## Controller Unit

## Parts List

|Part | Part Description  | Manufacturer | Part ID | Order URL |
| ---- | ----------------- | ------------ | ------- | --------- |
| U1 | Microchip PIC18F23K20 MPU | Microchip  | 666-9860 | [RS Components](https://de.rs-online.com/web/p/mikrocontroller/6669860) |
| U2 |  L297D Stepper Motor Driver SOIC | STMicroelectronics  | 102-3535  | [RS Components](https://de.rs-online.com/web/p/motor-treiber-ics/1023535) |
| U3 | L298P013TR Dual Full Bridge Driver | STMicroelectronics | 880-5308 | [RS Components](https://de.rs-online.com/web/p/motor-treiber-ics/8805308) |
| U4 | SMD 3.3V Regulator TLV111733 | Texas Instruments | 923-3827 | [RS Components](https://de.rs-online.com/web/p/spannungsregler/9233827) |
| U5 |  L78S05CV 5V Regulator TO220 | STMicroelectronics  | 179345  | [Conrad](https://www.conrad.de/de/p/stmicroelectronics-l78s05cv-spannungsregler-linear-typ78-to-220ab-positiv-fest-5-v-2-a-179345.html) |
| D1-8 | Schottkey Diode SK26L | PanJit | 1304995 | [Conrad](https://www.conrad.de/de/p/panjit-schottky-diode-gleichrichter-sk26l-do-214aa-60-v-einzeln-1304995.html) |
| R1,2 | Resistor SMD 1206 1 Ohm 1/2W | Panasonic | 1473248 | [Conrad](https://www.conrad.de/de/p/panasonic-erj-8bqf1r0v-dickschicht-widerstand-1-smd-1206-0-5-w-1-200-ppm-c-1473248.html) |
| R3 | Resistor SMD 0805 22k Ohm 1/8W| Tru Components | 1584677 | [Conrad](https://www.conrad.de/de/p/dickschicht-widerstand-22-k-smd-0805-0-125-w-5-100-ppm-c-tru-components-tc-0805s8j0223t5e203-1-st-1584677.html) |
| R5 | Resistor SMD 0805 3.3k Ohm 1/8W| Tru Components | 1584493 | [Conrad](https://www.conrad.de/de/p/tru-components-tc-0805s8f3301t5e203-dickschicht-widerstand-3-3-k-smd-0805-0-125-w-1-100-ppm-c-1-st-tape-cut-1584493.html) |
| R4,6-13 | Resistor SMD 0805 2.2k Ohm 1/8W| Tru Components | 1584491 | [Conrad](https://www.conrad.de/de/p/tru-components-tc-0805s8f2201t5e203-dickschicht-widerstand-2-2-k-smd-0805-0-125-w-1-100-ppm-c-1-st-tape-cut-1584491.html) |
| C1 | Capacitor SMD 0805 3300pF | Thomsen | 460338 | [Conrad](https://www.conrad.de/de/p/thomsen-keramik-kondensator-smd-0805-3300-pf-50-v-10-1-st-tape-cut-460338.html) |
| C2,3,5,7 | Capacitor SMD 0805 100nF 50V  | Samsung | 454108 | [Conrad](https://www.conrad.de/de/p/samsung-electro-mechanics-cl21b104jbcnnnc-keramik-kondensator-smd-0805-100-nf-50-v-5-4000-st-tape-on-full-reel-454108.html?searchType=SearchRedirect) |
| C4 | Elecrolytic Capacitor 470uF 16V| Yageo | 445373 | [Conrad](https://www.conrad.de/de/p/yageo-se016m0470b3f-0811-elektrolyt-kondensator-radial-bedrahtet-3-5-mm-470-f-16-v-20-x-h-8-mm-x-12-mm-1-st-445373.html) |
| C6 | Elecrolytic Capacitor 100uF 16V| Yageo | 445579 | [Conrad](https://www.conrad.de/de/p/yageo-s5016m0100bzf-0605-elektrolyt-kondensator-radial-bedrahtet-2-5-mm-100-f-16-v-20-x-h-6-mm-x-5-mm-1-st-445579.html) |
| J1-6 | Pin Strip Header 8Pin 3A| BKL Electronic | 742235-VQ | [Conrad](https://www.conrad.com/p/bkl-electronic-10120504-straight-nominal-current-details-3-a-742235) |
| J4 | 90° D9M connector | MH Connectors | 747176-VQ | [Conrad](https://www.conrad.de/de/search.html?search=747176%20-%20VQ) |
| J8 | Low Power connector Socket 2.1mm 5.5mm | BKL Electronic | 733946 | [Conrad](https://www.conrad.com/p/bkl-electronic-072335-low-power-connector-socket-vertical-vertical-55-mm-21-mm-1-pcs-733946) |
| J9 | BNC Connector Socket | TRU COMPONENTS | 1564888 | [Conrad](https://www.conrad.com/p/tru-components-740632-bnc-connector-socket-vertical-vertical-50-1-pcs-1564888) |
| Box | ABS Case 121x94x34mm  | Hammond | 493-6032 | [RS Components](https://de.rs-online.com/web/p/universalgehause/4936032) |
| LCD | LCD 16x2 White on Blue  | Gleichmann | 183045 | [Conrad](https://www.conrad.com/p/gleichmann-led-component-white-blue-w-x-h-x-d-80-x-36-x-132-mm-ge-c1602b-tmi-jtr-183045) |
| SW1-4 | Momentary Switch TC-D6SW  | TRU COMPONENTS | 2238782 | [Conrad](https://www.conrad.de/de/p/tru-components-tc-d6sw-impulstaster-35-v-dc-0-01-a-tastend-1-st-1589415.html) |
| PCB | Strip Board Paper/Copper 2.54mm | Rademacher | 529531-62 | [Conrad](https://www.conrad.de/de/p/rademacher-wr-typ-710-2-platine-hartpapier-l-x-b-100-mm-x-75-mm-35-m-rastermass-2-54-mm-inhalt-1-st-529531.html) |
| PSU | Plugin Powersupply 9V 2A  | Mean Well | 1837961 | [Conrad](https://www.conrad.de/de/p/mean-well-gsm18e09-p1j-steckernetzteil-festspannung-9-v-dc-2-a-18-w-1837961.html#productTechData) |

liquid feeder schematic<br/>
**Liquid Feeder Schematic**

liquid feeder PCB<br/>
**Liquid Feeder PCB**

## 1. PCB Assembly

PCB Gerber files are supplied allowing production and ordering, the origional Proteus design file is also supplied incase any modifications for specific requirements are necessary.
All components of the PCB are mounted by hand and special attention should be applied to the motor driver (U3) as the underside of the component is used as a heat sink and must be soldered to the PCB,
this is done from the reverse side of the PCB using the through holes integrated on the PCB design.

## 2. LCD Preparation

The LCD requires that a few jumpers and components are added directly to the LCD module, this reduces the amount of connections between the main PCB and the LCD,
the schematic below shows the necessary modifications.
LCD mod<br/>
**LCD Schematic**

LCD PCB<br/>
**LCD Modification**: Shows how components are directly mounted to LCD module.

## 3. Controller assembly

All components are mounted in a plastic housing and necessary holes for the the LCD, switches and connectors are drilled accordingly.
control front<br/>
**Front Panel**: Showing LCD unit and the four buttons for operation.

control back<br/>
**Back Panel**: Showing connection to feeder unit(D9), trigger input(BNC), on/off switch and power connector(low power connector).

switches schematic<br/>
**Switches Schematic**: Showing connections between front panel switches and main PCB.

buttons side<br/>
**Button Mounting**: A peice of Strip board is used to mount the switches inside the case.

PCB mounting<br/>
**LCD/Buttons**: The LCD is simply held in place with hot glue.

controller open<br/>
**Finished Controller**: The main PCB is mounted inside the housing.

d9controller<br/>
**Controller wiring** From main PCB to D9 connector.

## 4. Programming

The Microprocessor must be programmed with the included program, this is performed using a Microchip Pickit 3 In-Circuit Debugger/Programmer and the Microchip MPLAB IDE X software,
once the included project is added to the programming software the PicKit programmer can be plugged directly into the J1 on the main PCB and the program uploaded to the microprocessor.

## Feeder unit

## Feeder Parts List

|Part | Part Description  | Manufacturer | Part ID | Order URL |
| ---- | ----------------- | ------------ | ------- | --------- |
| M1 | Stepper Motor 0.25Nm 0.6A | EMIS | 198398 | [Conrad](https://www.conrad.de/de/p/emis-schrittmotor-103-h5205-0351-103-h5205-0351-0-25-nm-0-6-a-wellen-durchmesser-5-mm-198398.html) |
| SW5,6 | Microswitch125V AC 3A| Hartmann | 704713 | [Conrad](https://www.conrad.de/de/p/hartmann-mikroschalter-microhart-125-v-ac-3-a-1-x-ein-ein-tastend-1-st-704713.html) |
| Rod | Threaded Rod M3 500mm  | REELY | 297984 | [Conrad](https://www.conrad.de/de/p/reely-297984-gewindestange-m3-500-mm-messing-1-st-297984.html) |
| Spacer | 10mm M3 Brass Spacer  | Elektromechanik Schaefer GmbH| 526630 | [Conrad](https://www.conrad.com/p/603510-b6-spacer-l-10-mm-m3-m3-brass-1-pcs-526630) |
| J10 | D-Sub Connector 9pin Female  | Molex | 2447529 | [Conrad](https://www.conrad.de/de/p/molex-1727040168-fct-standard-density-d-sub-connector-female-straight-solder-cup-gold-plating-200-mating-cycles-15-2447529.html) |
| Cable | D-Sub9 Cable M-F 2M  | Pheonix Contact | 673801 | [Conrad](https://www.conrad.de/de/p/phoenix-contact-seriell-parallel-anschlusskabel-1x-d-sub-buchse-15pol-1x-d-sub-stecker-15pol-2-00-m-weiss-673801.html) |
| Wire | Jumper Wire 1x0.2mm  | Tru Components | 1567899 | [Conrad](https://www.conrad.de/de/p/tru-components-1567899-schaltdraht-yv-1-x-0-20-mm-schwarz-100-m-1567899.html) |

## 1. Parts Preparation

The motor (M1) has an output shaft which requires modification, this is best performed on a lathe, The motor should be carefully dismantled and the rotor removed.

1. Using a lathe the shaft of the rotor should be shortened to the same length as the shorter side of the rotor meaning the assembled motor has no protruding shaft from either side.
2. Using a lathe the complete length of the rotor/shaft should be drilled out using a 2.5mm drill bit mounted in the tailstock,
it is very important that the drilling is centered correctly for smooth operation and this can be achieved by using a centre drill first as a guide before the 2.5mm drill bit.
3. Using a lathe an M3 thread must be cut within the hole drilled in step two, the M3 Tap should be mounted in the tailstock and the tailstock should be freely moving on the guide ways,
by turning the main spindle chuck holding the rotor by hand the thread can be accurately cut through the entire length of the rotor shaft.
4. The four screws holding the motor together should be replaced with M3x35 screws or shortened to 35mm length.
5. The motor should now be reassembled paying particular care to making sure there is no small pieces of metal swarf trapped within and all parts are sufficiently clean,
any dirt or swarf will cause the motor to jam. The motor cover (1) should be mounted to the motor using the replacement M3x35 screws.

A piece of brass M3 threaded rod should be cut to a length of 83mm and the threads cleaned on each end.

Once all parts are 3D printed a small amount of cleaning/trimming and sanding is required to allow the slider (5)
to move freely within the main body (6) and all parts to accurately fit together without force. The following drawing shows all parts for assembly.

assembly<br/>
**Complete Assembly**

## 2. Assembly of parts

The 10mm M3 spacer is inserted into the slot on the slider (5) so that the internal thread can be seen through the hole,
the threaded brass rod should then be inserted into the hole and screwed into the inserted spacer, it is necessary to apply some thread lock to stop the threaded rod from unscrewing itself during operation.

sliderpic<br/>
**Assembled slider**

The slider (5) can now be inserted into the main body (6), be sure that the slider is free moving in its guide ways for the full extent of its movement.
A small amount of general purpose grease is recommended to be applied to the guideway and slider as well as the threaded rod.

The motor mount (3) can now be mounted to the body (6) and secured using two countersunk 3x10mm self tapping screws.

With the slider (6) retracted so that the threaded rod is at its longest the motor (2) can be screwed onto the threaded rod as far as it will go before touching the motor mount (3),
the motor (2) can now be pushed until it is seated with the motor mount (3) and secured using four M3x10 screws.

The syringe lock (7) can be secured to the body (6) using a M3x10 screw,
this should not be too tight as it is required to rotate and either lock the syringe in place or unlock the syringe for replacement or cleaning.

The two end stop microswitches (4,8) can be slid on to the mounting guide pins, care must be taken doing this as the guide pins are quite fragile.

The D9 connector (9) can be mounted into the back cover (10).

Wires should be connected to the two microswitches (4,8) and connected to the D9 connector as shown in the wiring diagram below.
The wires from the motor should be shortened and also connected to D9 connector as shown in the wiring diagram.

Wiring<br/>
**Feeder wiring schematic:** showing connection between motor and empty/full switches to D9 male connector.

The back cover can now be fitted in place paying close attention that any wires are not in the path of the slider.
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

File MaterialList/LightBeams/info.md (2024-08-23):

# Light Barrier

## 1. Description

The light barrier is designed to detect any interruption in the light path between the LED (light emmiting diode) emitter and the Photo transistor and convert this interruption into a TTL-compatible
logic level (Transistor-Transistor-Logic ) output for the duration of the interruption.

The light barrier has many applications for the detection of movement of many different things such as people, animals, mechanical parts or to stop a motor in a required preset position for example.
The TTL output can  be used to control other logical operations either in discreet electronics or using microprocessors and single board computers such as the Raspberry Pie or  Arduino as an example.
Most modern processors run on 3.3V but are tolerant of TTL levels which are 5V. If the higher 5V can not be tolerated then a level shifter should be added to the schematic.

## 2. Parts List
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

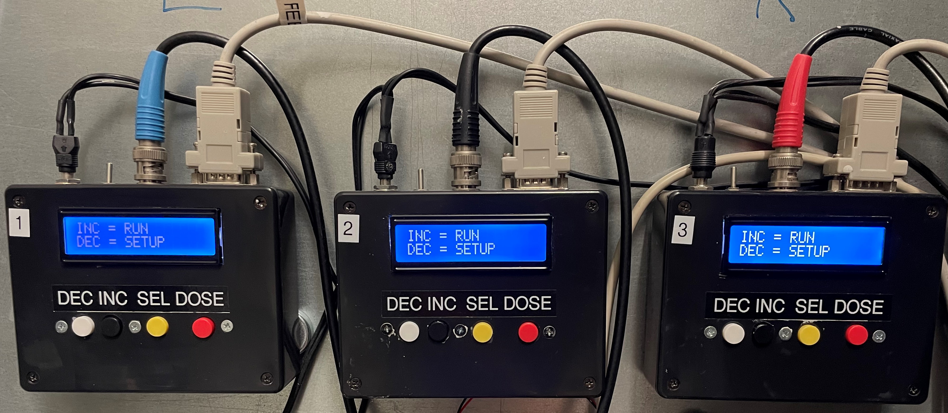
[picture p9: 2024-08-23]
MaterialList/FoodDispensers/graphics/controllers.jpg

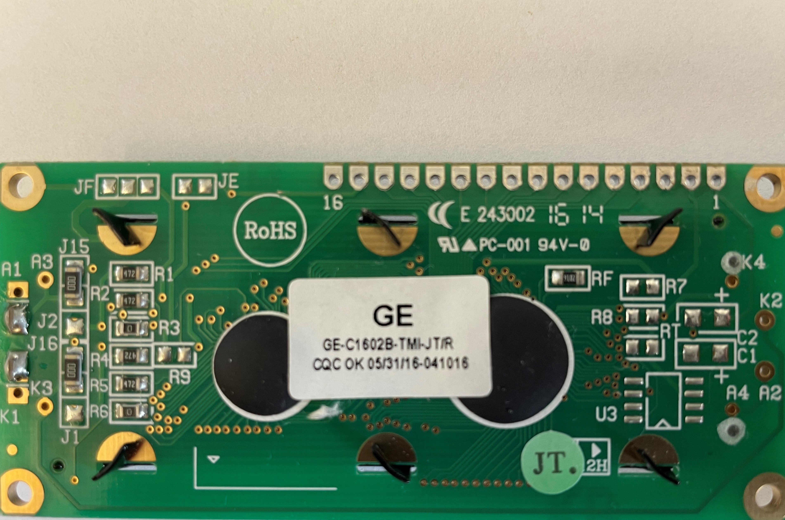
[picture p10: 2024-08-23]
MaterialList/FoodDispensers/graphics/spare pics/LCD.jpg

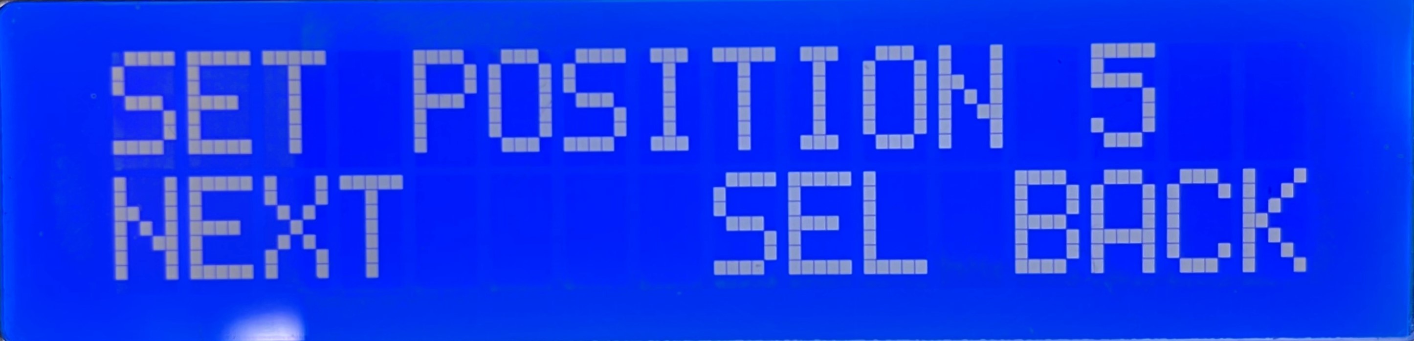
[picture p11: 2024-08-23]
MaterialList/ApertureGate/graphics/pos5.JPG

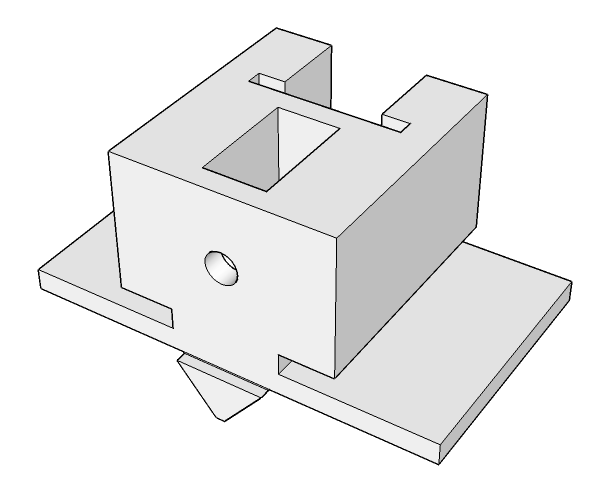
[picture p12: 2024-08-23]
MaterialList/FoodDispensers/graphics/spare pics/slider.png

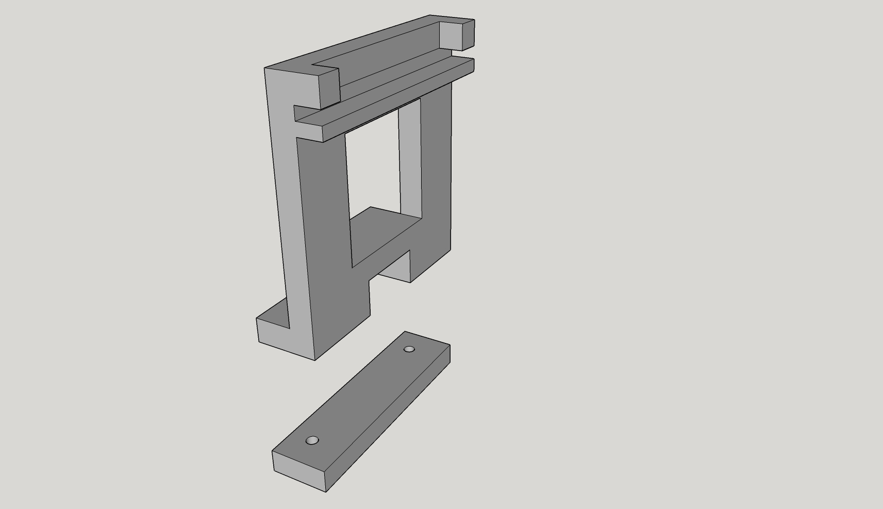
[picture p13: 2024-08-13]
MaterialList/Mount and track support.jpg

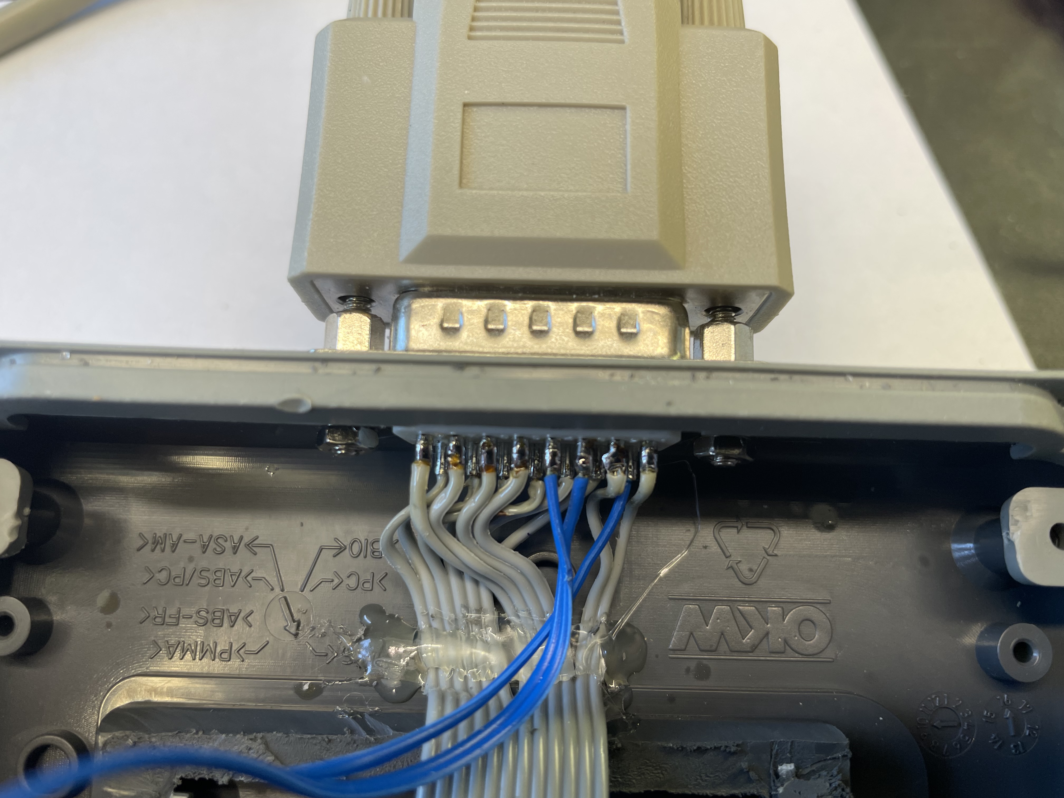
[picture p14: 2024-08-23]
MaterialList/ApertureGate/graphics/caseopen5.JPG

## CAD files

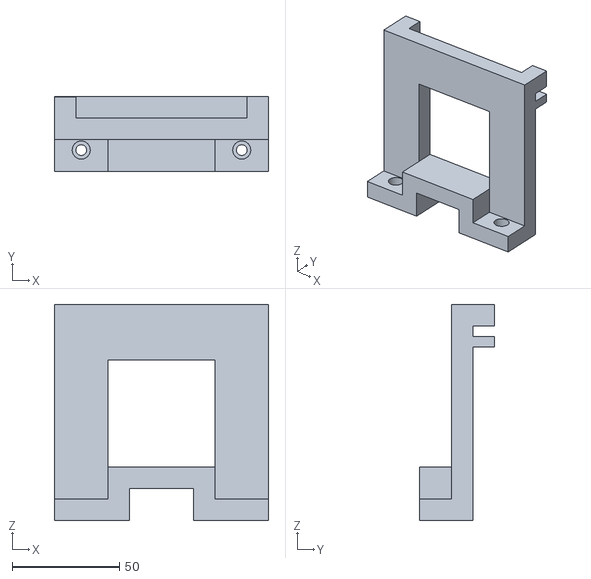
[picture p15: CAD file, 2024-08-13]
MaterialList/Mount and track support 1.stl
100.0 x 35.0 x 101.0

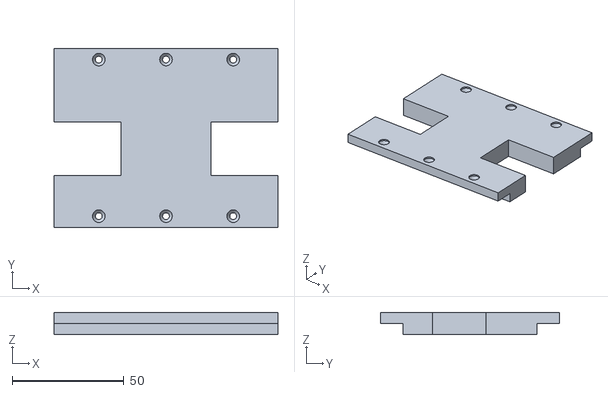
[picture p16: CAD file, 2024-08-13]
MaterialList/Transparent track.stl
100.0 x 80.0 x 10.0

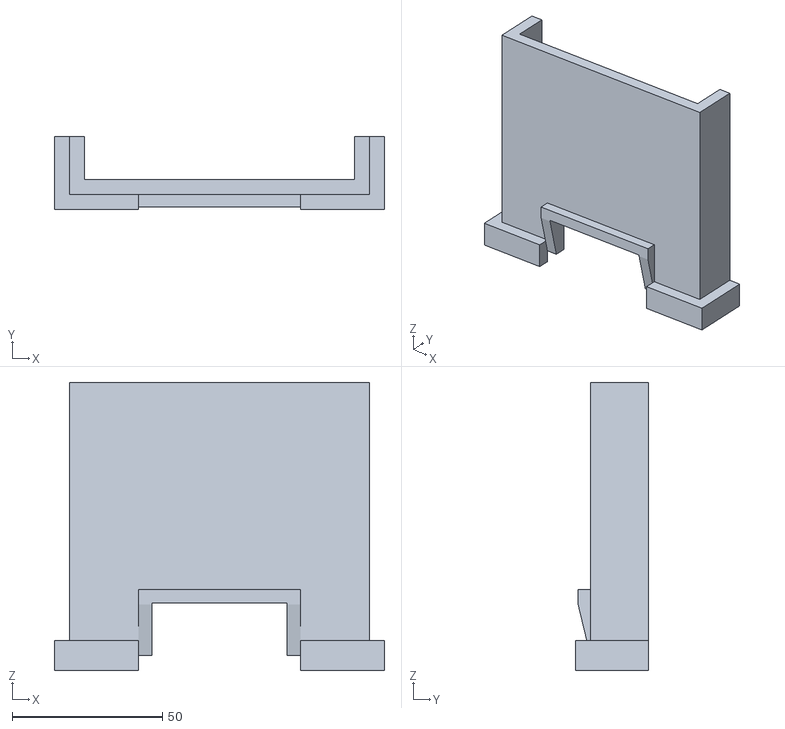
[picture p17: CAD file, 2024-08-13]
MaterialList/Track end wall.stl
110.0 x 24.4 x 96.0

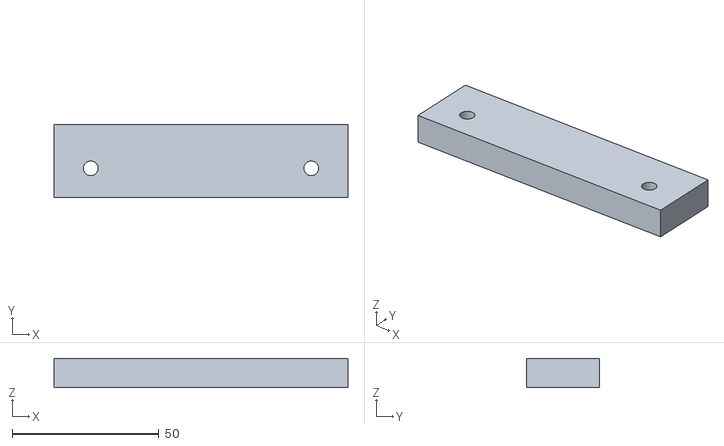
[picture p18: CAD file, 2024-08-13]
MaterialList/Mount and track support 2.stl
100.0 x 25.0 x 10.0

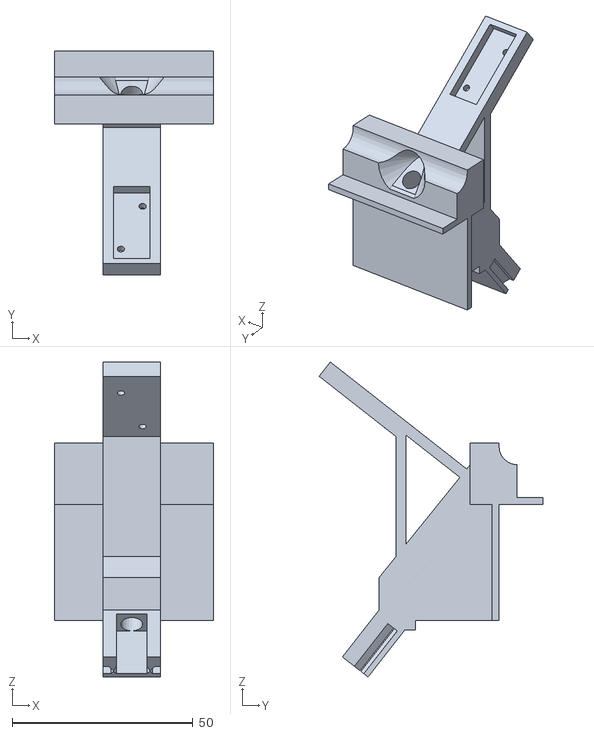
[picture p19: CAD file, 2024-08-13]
MaterialList/Lickport.stl
44.0 x 61.8 x 87.0

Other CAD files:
MaterialList/ApertureGate/cad/aperture doors master.skp
MaterialList/FoodDispensers/cad/microdispensor master.skp
MaterialList/LightBeams/cad/light barrier master.skp

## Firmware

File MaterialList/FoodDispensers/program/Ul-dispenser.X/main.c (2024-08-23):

/******************************************************************************/
/**********              File:  ULitre_dispenser.c             ****************/
/**********     Author: Lee Embray, Heidelberg Universität     ****************/
/**********  Physiology und Pathophysiology abteilung          ****************/
/**********           Created on 16. October 2017,             ****************/
/******************************************************************************/

/******************************************************************************/
/********************************* DEFINE *************************************/
/******************************************************************************/
#define RS RA2                                                                  // LCD Register Select pin
#define EN RA3                                                                  // LCD Enable pin 
#define D4 RA4                                                                  // LCD DATA 0
#define D5 RA5                                                                  // LCD DATA 1                 
#define D6 RA6                                                                  // LCD DATA 2
#define D7 RA7                                                                  // LCD DATA 3

#define DOSE RB0                                                                // LCD Register Select pin
#define MEN RB1                                                                 // LCD Enable pin 
#define MCLK RB2                                                                // LCD DATA 0
#define MCW RB3                                                                 // LCD DATA 1                 
#define MH RB4                                                                  // LCD DATA 2
#define INC RC0                                                                 // LCD DATA 3  
#define DEC RC1                                                                 // LCD DATA 3 
#define SEL RC2                                                                 // LCD DATA 3 
#define TRIG RC3                                                                // LCD DATA 3 
#define SPOUT1 RC4                                                              // LCD DATA 3 
#define SPOUT2 RC5                                                              // LCD DATA 3 
#define FULL RC6                                                                // LCD DATA 3 
#define EMPTY RC7                                                               // LCD DATA 3 
/******************************************************************************/
/******************************** INCLUDE *************************************/
/******************************************************************************/
#include "mcc_generated_files/mcc.h"
#include "lcd.h"
#include <stdio.h>
#include <time.h>
#include <stdlib.h>
/******************************************************************************/
/************************** DEFINE VARIABLES **********************************/
/******************************************************************************/
unsigned int quantity;
unsigned int steps;
unsigned int quantitytemp;
unsigned int stepstemp;
unsigned int check;
unsigned eeprom char address1 = 0x10;
char s[20];
/**************************** FUNCTION ****************************************/
/************************** DELAY 200mS ***************************************/
/******************************************************************************/
void delay(void)                                                                // function for 200mS delay
{
    __delay_ms(100);
    __delay_ms(100);
}
/**************************** FUNCTION ****************************************/
/************************** DELAY 500mS ***************************************/
/******************************************************************************/
void delay5(void)                                                               // function for 500mS delay
{
    __delay_ms(100);
    __delay_ms(100);
    __delay_ms(100);
    __delay_ms(100);
    __delay_ms(100);
}
/****************************** FUNCTION **************************************/
/****************** eeprom save function 8bit number **************************/
/******************************************************************************/
void eepromsave(void)                                                           // function for saving the values to non volatile memory
{   
DATAEE_WriteByte(address1, quantity);
}
/****************************** FUNCTION **************************************/
/***************** eeprom load delay function 8bit number *********************/
/******************************************************************************/
void eepromload(void)                                                           // function for loading the values from non volatile memory
{ 
quantity = DATAEE_ReadByte(address1);
 }
/**************************** FUNCTION ****************************************/
/************************** set quantity **************************************/
/******************************************************************************/
void SETQUANTITY(void)                                                          // function for setting the pulse duration and to save in "trig1 and trig2"
{
delay5();                                                                        // anti bounce
Lcd_Clear();                                                                    // clear the LCD    
while(SEL != 0)                                                                 // until select button is pressed stay in function "PULSE SET"
    {
    if(quantity > 250)                                                          // if time is out of range then set to 250
        quantity = 250;
    sprintf(s, "QUANTITY=%u Ul", quantity);                                     // make s = "time"
    Lcd_Set_Cursor(1,1);                                                        // set LCD cursor to line 1 position 1
    Lcd_Write_String(s);                                                        // write text "s" to line 1
    if(INC == 0 && quantity < 250)                                              // allow maximum of 250mSec                     
        {                      
        quantity = quantity+1;                                                  // if left button pressed then increment "time" by 1
        __delay_ms(30);                                                         // set delay to fix key bounce and auto increment on hold speed
        Lcd_Clear();                                                            // clear the LCD 
        }   
    if(DEC == 0 && quantity > 1)                                                // allow minimum of 1mSec
        {
        quantity = quantity-1;                                                  // if right button pressed then decrement "time" by 1
        __delay_ms(30);                                                         // set delay to fix key bounce and auto increment on hold speed
        Lcd_Clear();                                                            // clear the LCD                                                        
        }
    quantitytemp = quantity;                                                // save time in temp
    }
Lcd_Clear();                                                                    // clear LCD
eepromsave();                                                                   // save all values to eeprom using eepromsave function
}
/**************************** FUNCTION ****************************************/
/***************************** EMPTY ******************************************/
/******************************************************************************/
void EMPTYSYRINGE(void)                                                         // menu function for selecting amount to dispense
{
Lcd_Clear();
Lcd_Set_Cursor(1,1);                                                            // set LCD cursor on line 1 position 1
Lcd_Write_String("EMPTYING SYRINGE");                                           // write text to line 1
Lcd_Set_Cursor(2,1);                                                            // set LCD cursor on line 1 position 1
Lcd_Write_String("SEL = STOP");                                                 // write text to line 1
MCW = 0;                                                                        // SET MOTOR TO CLOCKWISE
MEN = 1;                                                                        // ENABLE MOTOR
while(SEL != 0 && EMPTY != 0)                                                   // until select button is pressed stay in function "EMPTY FILL"
    {
    MCLK = 1;                                                                   // SEND PULSES TO MOTOR
    __delay_us(500);
    MCLK = 0;
    __delay_us(500);
    }
MEN = 0;                                                                        // DISABLE MOTOR
Lcd_Clear();
}
/**************************** FUNCTION ****************************************/
/****************************** FILL ******************************************/
/******************************************************************************/
void FILLSYRINGE(void)                                                          // menu function for selecting amount to dispense
{
Lcd_Clear();
Lcd_Set_Cursor(1,1);                                                            // set LCD cursor on line 1 position 1
Lcd_Write_String("FILLING SYRINGE");                                            // write text to line 1
Lcd_Set_Cursor(2,1);                                                            // set LCD cursor on line 1 position 1
Lcd_Write_String("SEL = STOP");                                                 // write text to line 1
MCW = 1;                                                                        // SET MOTOR TO ANTI-CLOCKWISE 
MEN = 1;                                                                        // ENABLE MOTOR
while(SEL != 0 && FULL != 0)                                                    // until select button is pressed stay in function "EMPTY FILL"
    {           
    MCLK = 1;                                                                   // SEND PULSES TO MOTOR
    __delay_us(500);
    MCLK = 0;
    __delay_us(500);
    }
MEN = 0;                                                                        // DISABLE MOTOR
Lcd_Clear();
}
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

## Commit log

2024-07-08 Material list created
2024-07-25 Add files via upload
    AnimalData file for calcium imaging for the sample mouse. Use it in combination with Scripts_for_figures_calciumimaging.m.
2024-08-09 Adding 3D model blender files
    These are the .blend files for the 3D model of the Automated Tactile DIscrimination Setup
    [SalienceSetup.blend]
2024-08-13 Add setup drawings
    [Lickport.stl, Mount and track support 1.stl, Mount and track support 2.stl, Track end wall.stl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]
2024-08-23 Add files from bothlab
    [aperture doors master.skp, light barrier master.skp, microdispensor master.skp]
2024-08-24 Update dir names
    [light barrier master.skp, microdispensor master.skp]
